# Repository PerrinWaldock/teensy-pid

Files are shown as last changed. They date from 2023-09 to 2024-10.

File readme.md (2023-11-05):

# Teensy-based Intensity Feedback Controller Guide

This repository contains code and PCBs for creating Teensy microcontroller-based feedback controllers. They are used to control the laser intensity on Prometheus because (a) they are relatively inexpensive and (b) they provide faster rise times than similarly-priced analog feedback controllers.

## PCB-free Feedback Controller

The code in the `multistate` branch is currently installed in the Prometheus apparatus. It is running on a Teensy 3.2 because that microcontroller has 5V-tolerant digital inputs, and an inbuilt DAC. It uses two digital signals from the QDGBus digital outputs to select one of four setpoints which are configured over USB. It controls the voltage into a XM-B6H4-0404C-01.

However, this setup has some flaws:
* the inbuilt ADC and DAC are noisy, with only ~8-10 usable bits. This limits the feedback stability shown in the above posts.
* there is no input anti-aliasing filter
* the connections are soldered together on stripboard. The digital input controlling the LSB of the state is currently loose, so the feedback controller occasionally malfunctions when the digital input is not connected to the microcontroller
* the Teensy 3.2 is currently EOL so it is challenging to find a replacement.

A replacement PCB was built that provides the following features:
* input anti-aliasing filtering
* input and output buffering
* input over-voltage protection for both digital and analog inputs
* 16-bit ADCs and DACs
* a faster (600 MHz) microcontroller
* a separate +5V power supply for all analog electronics
* space on the board to mount an XM-B6H4-0404C-01.

The new PCB and its corresponding control code is in the `master` branch of the repository. Below is a guide to the PCB and control code:

## PCB Important Components
The KiCAD design files and schematics are in the schematics folder of this repository. Below is a guide to some components that can be populated or depopulated to change the performance characteristics of the board:
* R1: Populate this to give this board a 50-ohm terminated input. Useful when interfacing with a [PDA100A2](https://www.thorlabs.com/thorproduct.cfm?partnumber=PDA100A2) because they produce a 0-5V output when terminated with a 50 ohm load.
  * One can also modify the values of R1, R2 to remove a DC offset from the input signal, or modify the values of R7 and R9 to amplify the input. Useful if the input is a small signal.
* R3: Populate this to bypass the input op amp. Do not do this without first disconnecting the op amp from by depopulating R2 and R9. Often used when R15 and R17 are populated to use the internal ADC instead of the external ADC (not recommended).
* C1 and R7: Change these values to change the input op amp filter (currently not populated).
* R16 and R18. ONLY POPULATE ONE OF THESE AT A TIME. Used to select 5V or 3.3V reference. If 5V reference is selected (R18), make sure to depopulate R6 so that the input voltage range is the full 0V-5V.
* R34: Populate to use external 5V instead of USB 5V power. DO NOT DO THIS WITHOUT FIRST COVERING THE PIN THAT SUPPLIES POWER ON THE USB CABLE: https://community.octoprint.org/t/put-tape-on-the-5v-pin-why-and-how/13574
* R40: Populate to bypass the output buffer. Do not do this without first disconnecting the op amp by depopulating R41 and FB2.

## Software Important Preprocessor Directives
You can access the following directives in the arduinopid.h file:
* `OUTPUT_SETTLE_DELAY_US` should be set to the response time of the voltage variable attenuator. It is a delay that kicks in immediately after the set point changes from off to on.
  * When the output changes state from off (below the minimum set point) to on (between the minimum and maximum setpoint), the feedback calculation is skipped for the first output, and only the feedforward value is used. This allows the feedback controller to rapidly approach the desired value. However, it takes a finite amount of time for the system to reach the desired value. This delay stops the next feedback measurement from being taken before the system settles to its new state.
* `PIN_REFERENCE0` and `PIN_REFERENCE1` are used to select which preprogrammed set voltage the feedback controller will try to attain.
* `PIN_REFERENCE` can be used as a traditional analog setpoint (NOTE: The PCB is not currently set up to support this)
* `INPUT_MODE` sets the type of input that the feedback controller uses to select its state. `DIGITAL_INPUT` selects preprogrammed set voltage number `PIN_REFERENCE1*2 + PIN_REFERENCE0`, `ANALOG_INPUT` uses the voltage on `PIN_REFERENCE`, and `SOFTWARE_INPUT` only accepts software changes to the set voltage. Note that the `ANALOG_INPUT` mode is not currently well-tested.
  * It may be advantageous to reduce `ANALOGREFERENCERESOLUTION` to 8 or lower to speed up the loop frequency.
* `FEEDFORWARD` enables feedforward control. One can characterize the transfer function of the system via a serial command, then perform corrections to the feedforward function using PID. It generally produces faster rise times than standard PID feedback control.
* `NEGATIVE_OUTPUT` should be set to true if a larger output voltage should produce a smaller input voltage and vice versa.
* `LIMITED_SETPOINT` set to true means that PID control is only active within a certain setpoint range. Set to true to avoid integral wind-up when the output is set to zero or maximum. These
* `SAVE_DATA` will give the option to save PID constants, loop frequency, and feedforward data and load them on startup.

## Serial Commands
Connect the feedback controller using Putty or the Arduino IDE to tune the feedback parameters, adjust the setpoint, loop frequency, and other parameters.

Note that the FeedbackController class in the Prometheus repository uses some of the following serial commands in order to set the laser power to a certain level at specific points in a recipe.

Commands:
* `h` to print the help menu
* `kp=x` to set the proportional constant. `kp?` to print the proportional constant. Similar for `ki` and `kd`.
* `sv0=0.5` to set the 0th preprogammed set voltage to 0.5 volts. similar for `sv1`, `sv2`, and `sv3`. use `sv?` to view all for set voltages. Use `sp` to set the value as an integer instead of as a voltage.
* `ls=0.05` to set the minimum setpoint to 0.05V. Set to some value close to the minimum attainable feedback value. Used to prevent integral wind-up if the system cannot reach the set value.
* `ls=4.5` to set the maximum setpoint to 4.5V. Set to some value close to the maximum attainable feedback value. Used to prevent integral wind-up if the system cannot reach the set value.
* `lf=2000` to set the loop frequency to 2000 Hz. lf? to view the loop frequency. Make sure that the loop period is not less than the time the controller takes to perform a pid calculation.
* `ra=2` to set the number of read averages to four. The formula is <read averages>=2^x where x is an integer -- this ensures that the number of read averages is always a multiple of two, which speeds up the averaging process. Use ra? to view the number of read averages
* `pa=1` to enable feedback control, `pa=0` to disable it
* `po=1` to print sample feedback control values. `po=0` to disable the printed sample feedback control values. A sample string would be `s:6553	 f:6553	 ff:13490	 o:12850	 t:16`, where s refers to the set voltage, f is the feedback voltage, ff is the output voltage the feedforward term recommends, o is the output voltage of the controller, and t is the time the controller took to perform the feedback calculation. All voltages are written as integers, and the time is in microseconds. Write `po=2` to display the values as voltages instead.
* `cf=1` to create the feedforward function. Write `cd?` to print out the calibration data, and `ce?` to print out the calibration extrema (minimum and maximum set voltage).
* `ew=1` to write the feedback constants, loop rate, and calibration data to EEPROM so they are persistent after startup. `ew=0` to read all data from EEPROM. Useful when tuning to restore the feedback controller to a working state.
* `cl=1` to clear the integral term -- helpful if the integral term has spooled up.

Typical usage:
Via the USB serial connection, enter the following comnmands:
* `cf=1` (to calibrate the feedforward function)
* `ce?` (to print the minimum and maximum values that can theoretically be set)
* `sv0=1` (to set the set voltage to 1V. Replace the 1 with a value close to the maximum set voltage found above)
* `po=2` (monitor the output, ensure that it is stable)
* `po=0` (turn off the output)
* set the tuning parameters and loop frequency with `ki=x`,`kp=x`,`kd=0`, `lf=100000`. Ensure that the calculation time does not exceed the loop period. Adjust parameters until performance is satisfactory.

Some of these functions are implemented automatically in FeedbackController class in hardware/FeedbackController in the [Prometheus repository](https://qdg-code.phas.ubc.ca:2633/Perrin/PrometheusPython). This class automatically uses USB commands to assign different set voltages to different set voltage states during the recipe's compile time, then uses digital outputs to select those states while the recipe is executing. It automatically calibrates the feedforward function during compile time.

## Future Work To Do
### Speeding things up
Currently, the microcontroller is set to use a 600 MHz clock. Attaching a heatsink to the processor should allow high clock rates.

Higher clock rates may disrupt communication with the ADC and DAC. To improve the ADC and DAC throughput:
* connect an oscilloscope to the data lines as well as the analog output
* change "#define dacdigwr(p, s) digitalWrite(p, s)" in dac.ino to "#define dacdigwr(p, s) digitalWriteFast(p, s)"
* adjust WRITE_DELAY_NS such that the DAC still consistantly writes the correct value
* similarly, adjust WAIT_TIME_NS and CLOCK_DELAY_NS in adc.ino.
* R21, R22, R23, R24, R25, R26, R30, R31, and R32 may need to be adjusted to a smaller value to accommodate higher clock rates. Choose values that are as large as possible while still allowing the clock to remain high for the specified time in the ADC and DAC datasheets.

### Testing
* The latest version of the PCB (V3.0) has not been tested as a feedback controller for a laser intensity lock.
* Using the analog input as a setpoint also is not well-tested, and may contain bugs.

### New Algorithms
This controller should be usable for a gradient-descent saturated adsorption lock algorithm.

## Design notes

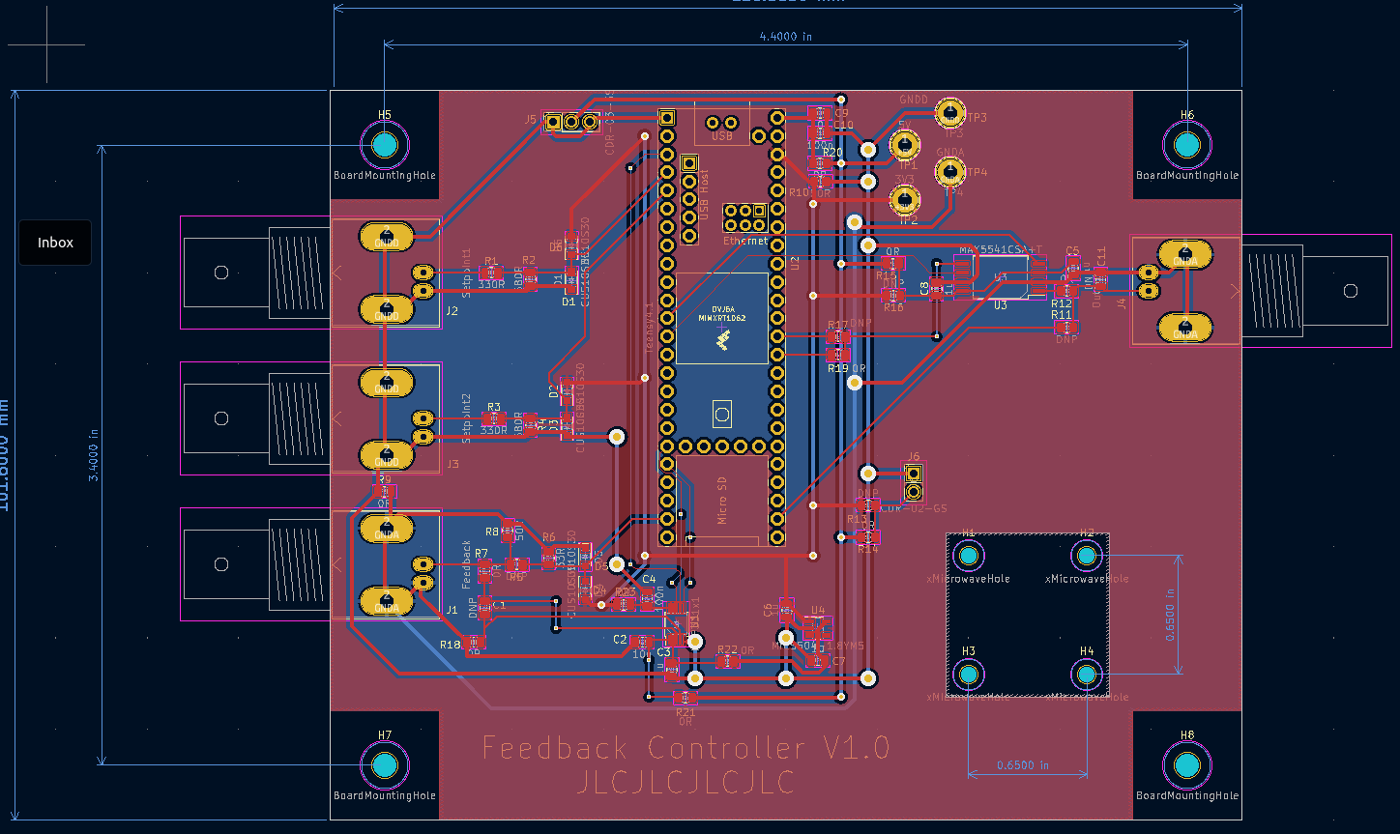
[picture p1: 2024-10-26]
schematics/schematics/feedbackControllerPCB.png

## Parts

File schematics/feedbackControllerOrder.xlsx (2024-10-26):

# | Reference | Qty | Value | Footprint | DNP | Link | Have | Need | Order | ordered
1 | C1, C18 | 2 | 30p | Capacitor_SMD:C_0805_2012Metric | DNP |  |  |  | 0
2 | C2, C6, C12, C15, C26, C28 | 6 | 10u | Capacitor_SMD:C_0805_2012Metric |  | https://www.digikey.ca/en/products/detail/samsung-electro-mechanics/CL21A106KOQNNNG/3894417 |  |  | 12
3 | C3, C5, C8, C9, C10, C13, C16, C25 | 8 | 100n | Capacitor_SMD:C_0805_2012Metric |  | https://www.digikey.ca/en/products/detail/samsung-electro-mechanics/CL21B104KBCNNNC/3886661 |  |  | 16
4 | C4, C20, C21 | 3 | 1n | Capacitor_SMD:C_0805_2012Metric |  | https://www.digikey.ca/en/products/detail/samsung-electro-mechanics/CL21B102KBANFNC/3888082 |  |  | 6
5 | C7, C11, C17, C19, C22, C23, C24, C29 | 8 | 1u | Capacitor_SMD:C_0805_2012Metric |  | https://www.digikey.ca/en/products/detail/samsung-electro-mechanics/CL21B105KAFNNNE/3886724 |  |  | 16
6 | C14 | 1 | 30p | Capacitor_SMD:C_0805_2012Metric |  | https://www.digikey.ca/en/products/detail/kyocera-avx/08055A300JAT2A/1602540 |  |  | 2
7 | C27 | 1 | 10n | Capacitor_SMD:C_0805_2012Metric |  | https://www.digikey.ca/en/products/detail/samsung-electro-mechanics/CL21B103KBANNNC/3886673 |  |  | 2
8 | D1, D2, D3, D4, D5, D6 | 6 | CUS10S30 | Diode_SMD:D_SOD-323_HandSoldering |  | https://www.digikey.ca/en/products/detail/toshiba-semiconductor-and-storage/CUS10S30-H3F/5114299 |  |  | 12
9 | FB1, FB2 | 2 | FerriteBead | Resistor_SMD:R_0805_2012Metric_Pad1.20x1.40mm_HandSolder |  | https://www.digikey.ca/en/products/detail/tai-tech-advanced-electronics-co-ltd/HFZ-2012PF-700T60/17835559 |  |  | 4
10 | H1, H2, H3, H4 | 4 | xMicrowaveHole | MountingHole:MountingHole_2.1mm |  | N/A |  |  | 8
11 | H5, H6, H7, H8 | 4 | BoardMountingHole | MountingHole:MountingHole_3.2mm_M3 |  | N/A |  |  | 8
12 | J1 | 1 | Feedback | Connector_Coaxial:BNC_Amphenol_B6252HB-NPP3G-50_Horizontal |  | Don’t Need |  |  | 2
13 | J2 | 1 | Setpoint1 | Connector_Coaxial:BNC_Amphenol_B6252HB-NPP3G-50_Horizontal |  | Don’t Need |  |  | 2
14 | J3 | 1 | Setpoint2 | Connector_Coaxial:BNC_Amphenol_B6252HB-NPP3G-50_Horizontal |  | Don’t Need |  |  | 2
15 | J4 | 1 | Output | Connector_Coaxial:BNC_Amphenol_B6252HB-NPP3G-50_Horizontal |  | Don’t Need |  |  | 2
16 | J5 | 1 | CDR-03-GS | Connector_PinSocket_2.54mm:PinSocket_1x03_P2.54mm_Vertical |  | Don’t Need |  |  | 2
17 | J6 | 1 | CDR-02-GS | Connector_PinHeader_2.54mm:PinHeader_1x02_P2.54mm_Vertical |  | Don’t Need |  |  | 2
18 | JP1, JP2, JP3 | 3 | SolderJumper_2_Open | Jumper:SolderJumper-2_P1.3mm_Open_Pad1.0x1.5mm |  | N/A |  |  | 6
19 | R1 | 1 | 50R | Resistor_SMD:R_0805_2012Metric | DNP |  |  |  | 0
20 | R2, R6, R7, R9, R13, R16, R19, R20, R28, R33, R34, R37, R41, R42, R43, R46 | 16 | 0R | Resistor_SMD:R_0805_2012Metric |  | https://www.digikey.ca/en/products/detail/stackpole-electronics-inc/RMCF0805ZT0R00/1756901 |  |  | 32
21 | R3, R18, R40, R44, R45 | 5 | 0R | Resistor_SMD:R_0805_2012Metric | DNP |  |  |  | 0
22 | R4, R15 | 2 | 1k | Resistor_SMD:R_0805_2012Metric | DNP |  |  |  | 0
23 | R5 | 1 | 350R | Resistor_SMD:R_0805_2012Metric |  | https://www.digikey.ca/en/products/detail/yageo/RC0805FR-07316RL/727856 |  |  | 2
24 | R8, R10, R27, R29 | 4 | 1k | Resistor_SMD:R_0805_2012Metric |  | https://www.digikey.ca/en/products/detail/stackpole-electronics-inc/RNCP0805FTD1K00/2240229 |  |  | 8
25 | R11 | 1 | 160R | Resistor_SMD:R_0805_2012Metric |  | https://www.digikey.ca/en/products/detail/koa-speer-electronics-inc/RK73H2ATTD1600F/10234348 |  |  | 2
26 | R12, R14 | 2 | 2k | Resistor_SMD:R_0805_2012Metric |  | https://www.digikey.ca/en/products/detail/stackpole-electronics-inc/RMCF0805FT2K00/1760249 |  |  | 4
27 | R17 | 1 | 2k | Resistor_SMD:R_0805_2012Metric | DNP |  |  |  | 0
28 | R21, R22, R23, R24, R25, R26, R30, R31, R32 | 9 | 10R | Resistor_SMD:R_0805_2012Metric |  | https://www.digikey.ca/en/products/detail/stackpole-electronics-inc/RMCF0805FT10R0/1760155 |  |  | 18
29 | R35 | 1 | 150R | Resistor_SMD:R_0805_2012Metric |  | https://www.digikey.ca/en/products/detail/koa-speer-electronics-inc/RK73H2ATTD1500F/10234167 |  |  | 2
30 | R36 | 1 | 100k | Resistor_SMD:R_0805_2012Metric | DNP |  |  |  | 0
31 | R38, R39 | 2 | 10k | Resistor_SMD:R_0805_2012Metric |  | https://www.digikey.ca/en/products/detail/vishay-dale/CRCW080510K0FKEAC/7928398 |  |  | 4
32 | TP1 | 1 | ADC_CONV | TestPoint:TestPoint_Loop_D2.50mm_Drill1.0mm |  | N/A |  |  | 2
33 | TP2 | 1 | ADC_DAT | TestPoint:TestPoint_Loop_D2.50mm_Drill1.0mm |  | N/A |  |  | 2
34 | TP3 | 1 | ADC_CLK | TestPoint:TestPoint_Loop_D2.50mm_Drill1.0mm |  | N/A |  |  | 2
35 | TP4 | 1 | DAC_CS | TestPoint:TestPoint_Loop_D2.50mm_Drill1.0mm |  | N/A |  |  | 2
36 | TP5 | 1 | DAC_DIN | TestPoint:TestPoint_Loop_D2.50mm_Drill1.0mm |  | N/A |  |  | 2
37 | TP6 | 1 | DAC_CLK | TestPoint:TestPoint_Loop_D2.50mm_Drill1.0mm |  | N/A |  |  | 2
38 | TP7 | 1 | +5V | TestPoint:TestPoint_Loop_D2.50mm_Drill1.0mm |  | N/A |  |  | 2
39 | TP8 | 1 | +3.3V | TestPoint:TestPoint_Loop_D2.50mm_Drill1.0mm |  | N/A |  |  | 2
40 | TP9 | 1 | GNDD | TestPoint:TestPoint_Loop_D2.50mm_Drill1.0mm |  | N/A |  |  | 2
41 | TP10 | 1 | GNDA | TestPoint:TestPoint_Loop_D2.50mm_Drill1.0mm |  | N/A |  |  | 2
42 | TP11 | 1 | +5VA | TestPoint:TestPoint_Loop_D2.50mm_Drill1.0mm |  | N/A |  |  | 2
43 | TP12 | 1 | +9V | TestPoint:TestPoint_Loop_D2.50mm_Drill1.0mm |  | N/A |  |  | 2
44 | U1, U6 | 2 | RS621 | Package_TO_SOT_SMD:SOT-23-5_HandSoldering |  | https://www.digikey.ca/en/products/detail/runic-technology/RS621KXF/14544643 |  |  | 4
45 | U2 | 1 | MCP331x1 | Package_SO:MSOP-10_3x3mm_P0.5mm |  | https://www.digikey.ca/en/products/detail/microchip-technology/MCP33131-10-E-MS/9757740 |  |  | 2
46 | U3 | 1 | TXU0104D | Package_SO:SOIC-14_3.9x8.7mm_P1.27mm |  | https://www.digikey.ca/en/products/detail/texas-instruments/TXB0104DR/1629101 |  |  | 2
47 | U4 | 1 | Teensy4.0 | Teensy:Teensy40 |  | https://www.digikey.ca/en/products/detail/sparkfun-electronics/DEV-15583/10384551 |  |  | 2
48 | U5 | 1 | MAX5541CSA+T | Package_SO:SOIC-8_3.9x4.9mm_P1.27mm |  | https://www.digikey.ca/en/products/detail/analog-devices-inc-maxim-integrated/MAX5541CSA-T/1780972 |  |  | 2
49 | U7 | 1 | MIC5504-3.3YM5 | Package_TO_SOT_SMD:SOT-23-5 |  | https://www.digikey.ca/en/products/detail/microchip-technology/MIC5504-1-8YM5-TR/5209404 |  |  | 2
50 | U8 | 1 | TC1014-2.5VCT713 | Package_TO_SOT_SMD:SOT-23-5 |  | https://www.digikey.ca/en/products/detail/microchip-technology/TC1014-2-5VCT713/443102 |  |  | 2
51 | U9 | 1 | TC1014-1.8VCT713 | Package_TO_SOT_SMD:SOT-23-5 |  | https://www.digikey.ca/en/products/detail/microchip-technology/TC1014-1-8VCT713/443100 |  |  | 2
52 | U10 | 1 | NJM2882F05-TE1 | Package_TO_SOT_SMD:SOT-23-5_HandSoldering |  | https://www.digikey.ca/en/products/detail/nisshinbo-micro-devices-inc/NJM2882F05-TE1/10671911 |  |  | 2
53 | U11 | 1 | IB0509LS-1WR3 | Misc:IB05_LS-1WR3 |  | https://www.digikey.ca/en/products/detail/mornsun-america-llc/IB0509LS-1WR3/16571428?s=N4IgTCBcDaIJICEAMBWJBOAMgZQLQEYB1AJQGYQBdAXyA |  |  | 2

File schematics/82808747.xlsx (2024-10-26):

# | QUANTITY | PART NUMBER | MANUFACTURER PART NUMBER | DESCRIPTION | CUSTOMER REFERENCE | BACKORDER | UNIT PRICE | EXTENDED PRICE
1 | 2 | 1568-DEV-20359-ND | DEV-20359 | TEENSY 4.1 WITHOUT ETHERNET |  | 0 | 43.56 | 87.12
2 | 3 | MCP33131-10-E/MS-ND | MCP33131-10-E/MS | IC ADC 16BIT SAR 10MSOP |  | 0 | 7.5 | 22.50
3 | 3 | MAX5541CSA+TCT-ND | MAX5541CSA+T | IC DAC 16BIT V-OUT 8SOIC |  | 0 | 21.26 | 63.78
4 | 5 | 576-4879-1-ND | MIC5504-1.8YM5-TR | IC REG LINEAR 1.8V 300MA SOT23-5 |  | 0 | 0.24 | 1.20
5 | 10 | 3565-RS621KXFCT-ND | RS621KXF | IC CMOS 1 CIRCUIT SOT23-5 |  | 0 | 0.678 | 6.78
6 | 20 | CUS10S30H3FCT-ND | CUS10S30,H3F | DIODE SCHOTTKY 30V 1A USC |  | 0 | 0.363 | 7.26
7 | 12 | WM5514-ND | 0731375003 | CONN BNC RCPT R/A 50 OHM PCB |  | 0 | 3.45 | 41.40
8 | 10 | 2057-CDR-03-TS-ND | CDR-03-TS | HEADER VERT TH TIN 3POS .1" SING |  | 0 | 0.258 | 2.58
9 | 3 | 2057-CDR-02-GS-ND | CDR-02-GS | HEADER VERT TH GOLD 2POS .1" SIN |  | 0 | 0.25 | 0.75
10 | 5 | 2057-CDH-02-ND | CDH-02 | CONN PLUG HSG 2POS 2.54MM |  | 0 | 0.25 | 1.25
11 | 10 | 2057-CDH-C-G-RCT-ND | CDH-C-G-R | CONTACT CRIMP FOR CDH-XX GOLD |  | 0 | 0.241 | 2.41
12 | 10 | 1276-2424-1-ND | CL21B102KBANFNC | CAP CER 1000PF 50V X7R 0805 |  | 0 | 0.056 | 0.56
13 | 20 | 1276-6455-1-ND | CL21A106KOQNNNG | CAP CER 10UF 16V X5R 0805 |  | 0 | 0.104 | 2.08
14 | 20 | 1276-1066-1-ND | CL21B105KAFNNNE | CAP CER 1UF 25V X7R 0805 |  | 0 | 0.091 | 1.82
15 | 10 | 13-RC0805FR-10330RLCT-ND | RC0805FR-10330RL | RES 330 OHM 1% 1/8W 0805 |  | 0 | 0.036 | 0.36
16 | 10 | 311-680CRCT-ND | RC0805FR-07680RL | RES 680 OHM 1% 1/8W 0805 |  | 0 | 0.036 | 0.36
17 | 20 | 1276-1003-1-ND | CL21B104KBCNNNC | CAP CER 0.1UF 50V X7R 0805 |  | 0 | 0.062 | 1.24
18 | 10 | 2019-RK73H2ATTD18R0FCT-ND | RK73H2ATTD18R0F | RES 18 OHM 1% 1/4W 0805 |  | 0 | 0.055 | 0.55
19 | 10 | 2019-RK73H2ATTD30R9FCT-ND | RK73H2ATTD30R9F | RES 30.9 OHM 1% 1/4W 0805 |  | 0 | 0.055 | 0.55
20 | 10 | RNCP0805FTD49R9CT-ND | RNCP0805FTD49R9 | RES 49.9 OHM 1% 1/4W 0805 |  | 0 | 0.105 | 1.05
21 | 10 | 2019-RK73H2ATTD1600FCT-ND | RK73H2ATTD1600F | RES 160 OHM 1% 1/4W 0805 |  | 0 | 0.055 | 0.55
22 | 50 | RMCF0805ZT0R00CT-ND | RMCF0805ZT0R00 | RES 0 OHM JUMPER 1/8W 0805 |  | 0 | 0.0144 | 0.72
23 | 10 | RNCP0805FTD1R00CT-ND | RNCP0805FTD1R00 | RES 1 OHM 1% 1/4W 0805 |  | 0 | 0.105 | 1.05

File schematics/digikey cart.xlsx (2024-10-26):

Index | Quantity | Part Number | Manufacturer Part Number | Description | Customer Reference | Available | Backorder | Unit Price | Extended Price CAD
1 | 4 | 2057-RF1-01K-D-00-50-BK-HDW-ND | RF1-01K-D-00-50-BK-HDW | BNC RA PCB 50 4GHZ ZINC BODY NI |  | 4 | 0 | 3.48 | 13.92
2 | 2 | MAX5541CSA+-ND | MAX5541CSA+ | IC DAC 16BIT V-OUT 8SOIC |  | 2 | 0 | 20.7 | 41.40
3 | 2 | MCP33131D-10T-I/MSCT-ND | MCP33131D-10T-I/MS | IC ADC 16BIT SAR 10MSOP |  | 2 | 0 | 15.13 | 30.26
4 | 10 | 1276-1003-1-ND | CL21B104KBCNNNC | CAP CER 0.1UF 50V X7R 0805 |  | 10 | 0 | 0.065 | 0.65
5 | 20 | 1276-1066-1-ND | CL21B105KAFNNNE | CAP CER 1UF 25V X7R 0805 |  | 20 | 0 | 0.096 | 1.92
6 | 10 | 1276-6454-1-ND | CL21A106KAYNNNG | CAP CER 10UF 25V X5R 0805 |  | 10 | 0 | 0.188 | 1.88
7 | 10 | CUS10S30H3FCT-ND | CUS10S30,H3F | DIODE SCHOTTKY 30V 1A USC |  | 10 | 0 | 0.388 | 3.88
8 | 25 | RMCF0805ZT0R00CT-ND | RMCF0805ZT0R00 | RES 0 OHM JUMPER 1/8W 0805 |  | 25 | 0 | 0.02 | 0.50
9 | 5 | 2057-CDR-03-GS-ND | CDR-03-GS | HEADER VERT TH GOLD 3POS .1" SIN |  | 5 | 0 | 0.32 | 1.60
10 | 5 | 2057-CDR-02-GS-ND | CDR-02-GS | HEADER VERT TH GOLD 2POS .1" SIN |  | 5 | 0 | 0.26 | 1.30
11 | 10 | 13-RC0805FR-13330RLCT-ND | RC0805FR-13330RL | RES 330 OHM 1% 1/8W 0805 |  | 10 | 0 | 0.052 | 0.52
12 | 10 | 511-SDR10EZPF49R9CT-ND | SDR10EZPF49R9 | HIGH ANTI-SURGE THICK FILM CHIP |  | 10 | 0 | 0.408 | 4.08
13 | 10 | 311-680CRCT-ND | RC0805FR-07680RL | RES 680 OHM 1% 1/8W 0805 |  | 10 | 0 | 0.052 | 0.52
14 | 3 | 576-4879-1-ND | MIC5504-1.8YM5-TR | IC REG LINEAR 1.8V 300MA SOT23-5 |  | 3 | 0 | 0.27 | 0.81
15 | 3 | 2057-CDH-02-ND | CDH-02 | CONN PLUG HSG 2POS 2.54MM |  | 0 | 3 | 0.27 | 0.81
16 | 10 | 2057-CDH-C-G-RCT-ND | CDH-C-G-R | CONTACT CRIMP FOR CDH-XX GOLD |  | 10 | 0 | 0.253 | 2.53
17 | 10 | P19220CT-ND | ERJ-6DQJ1R0V | RES SMD 1 OHM 5% 1/2W 0805 |  | 10 | 0 | 0.322 | 3.22
18 | 10 | P19220CT-ND | ERJ-6DQJ1R0V | RES SMD 1 OHM 5% 1/2W 0805 |  | 10 | 0 | 0.322 | 3.22

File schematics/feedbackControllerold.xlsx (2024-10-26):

Source: | /home/perrin/pcsync/BCITUBC/electronics/SimpleFeedbackController/feedbackController/feedbackController.kicad_sch
Date: | Sat 19 Aug 2023 12:48:53 PM
Tool: | Eeschema 7.0.6-7.0.6~ubuntu22.04.1
Generator: | /usr/share/kicad/plugins/bom_csv_grouped_by_value.py
Component Count: | 73
Collated Components:
Item | Qty | Reference(s) | Value | LibPart | Footprint | Datasheet | DNP | soldered
1 | 1 | C1 | 1n | Device:C | Capacitor_SMD:C_0805_2012Metric | ~
2 | 4 | C2, C9, C12, C14 | 10u | Device:C | Capacitor_SMD:C_0805_2012Metric | ~
3 | 5 | C3, C5, C6, C7, C8 | 1u | Device:C | Capacitor_SMD:C_0805_2012Metric | ~
4 | 4 | C4, C10, C13, C15 | 100n | Device:C | Capacitor_SMD:C_0805_2012Metric | ~
5 | 1 | C11 | 1n | Device:C | Capacitor_SMD:C_0805_2012Metric | ~ | DNP
6 | 6 | D1, D2, D3, D4, D5, D6 | CUS10S30 | pspice:DIODE | Diode_SMD:D_SOD-323_HandSoldering | ~
7 | 4 | H1, H2, H3, H4 | xMicrowaveHole | Mechanical:MountingHole | MountingHole:MountingHole_2.1mm | ~
8 | 4 | H5, H6, H7, H8 | BoardMountingHole | Mechanical:MountingHole | MountingHole:MountingHole_3.2mm_M3 | ~
9 | 1 | J1 | Feedback | Connector:Conn_Coaxial | Connector_Coaxial:BNC_Amphenol_B6252HB-NPP3G-50_Horizontal | ~
10 | 1 | J2 | Setpoint1 | Connector:Conn_Coaxial | Connector_Coaxial:BNC_Amphenol_B6252HB-NPP3G-50_Horizontal | ~
11 | 1 | J3 | Setpoint2 | Connector:Conn_Coaxial | Connector_Coaxial:BNC_Amphenol_B6252HB-NPP3G-50_Horizontal | ~
12 | 1 | J4 | Output | Connector:Conn_Coaxial | Connector_Coaxial:BNC_Amphenol_B6252HB-NPP3G-50_Horizontal | ~
13 | 1 | J5 | CDR-03-GS | Connector:Conn_01x03_Pin | Connector_PinSocket_2.54mm:PinSocket_1x03_P2.54mm_Vertical | ~
14 | 1 | J6 | CDR-02-GS | Connector:Conn_01x02_Pin | Connector_PinHeader_2.54mm:PinHeader_1x02_P2.54mm_Vertical | ~
15 | 2 | R1, R3 | 330R | Device:R_US | Resistor_SMD:R_0805_2012Metric | ~
16 | 2 | R2, R4 | 680R | Device:R_US | Resistor_SMD:R_0805_2012Metric | ~
17 | 1 | R5 | 18R | Device:R_US | Resistor_SMD:R_0805_2012Metric | ~ | DNP
18 | 1 | R6 | 33R | Device:R_US | Resistor_SMD:R_0805_2012Metric | ~
19 | 1 | R7 | 160R | Device:R_US | Resistor_SMD:R_0805_2012Metric | ~
20 | 2 | R8, R10 | 50R | Device:R_US | Resistor_SMD:R_0805_2012Metric | ~
21 | 11 | R9, R14, R15, R18, R19, R20, R21, R22, R23, R24, R29 | 0R | Device:R_US | Resistor_SMD:R_0805_2012Metric | ~
22 | 1 | R11 | 1k | Device:R_US | Resistor_SMD:R_0805_2012Metric | ~ | DNP
23 | 4 | R12, R16, R17, R25 | 0R | Device:R_US | Resistor_SMD:R_0805_2012Metric | ~ | DNP
24 | 1 | R13 | DNP | Device:R_US | Resistor_SMD:R_0805_2012Metric | ~
25 | 2 | R26, R27 | 1R | Device:R_US | Resistor_SMD:R_0805_2012Metric | ~
26 | 1 | TP1 | 5V | Connector:TestPoint | TestPoint:TestPoint_Loop_D3.80mm_Drill2.0mm | ~
27 | 1 | TP2 | 3V3 | Connector:TestPoint | TestPoint:TestPoint_Loop_D3.80mm_Drill2.0mm | ~
28 | 1 | TP3 | GNDD | Connector:TestPoint | TestPoint:TestPoint_Loop_D3.80mm_Drill2.0mm | ~
29 | 1 | TP4 | GNDA | Connector:TestPoint | TestPoint:TestPoint_Loop_D3.80mm_Drill2.0mm | ~
30 | 1 | U1 | MCP331x1 | Jakub:MCP331x1 | Package_SO:MSOP-10_3x3mm_P0.5mm | https://ww1.microchip.com/downloads/en/DeviceDoc/MCP33131D-Data-Sheet-DS20005947B.pdf |  | x
31 | 1 | U2 | Teensy4.1 | Teensy:Teensy4.1 | Teensy:Teensy41
32 | 1 | U3 | MAX5541CSA+T | MAX5541:MAX5541CSA+T | SOIC127P600X175-8N | https://www.analog.com/media/en/technical-documentation/data-sheets/MAX5541.pdf |  | x
33 | 1 | U4 | MIC5504-1.8YM5 | Regulator_Linear:MIC5504-1.8YM5 | Package_TO_SOT_SMD:SOT-23-5 | http://ww1.microchip.com/downloads/en/DeviceDoc/MIC550X.pdf
34 | 2 | U5, U6 | ~ | Misc:RS621KXF | Package_TO_SOT_SMD:SOT-23-5_HandSoldering

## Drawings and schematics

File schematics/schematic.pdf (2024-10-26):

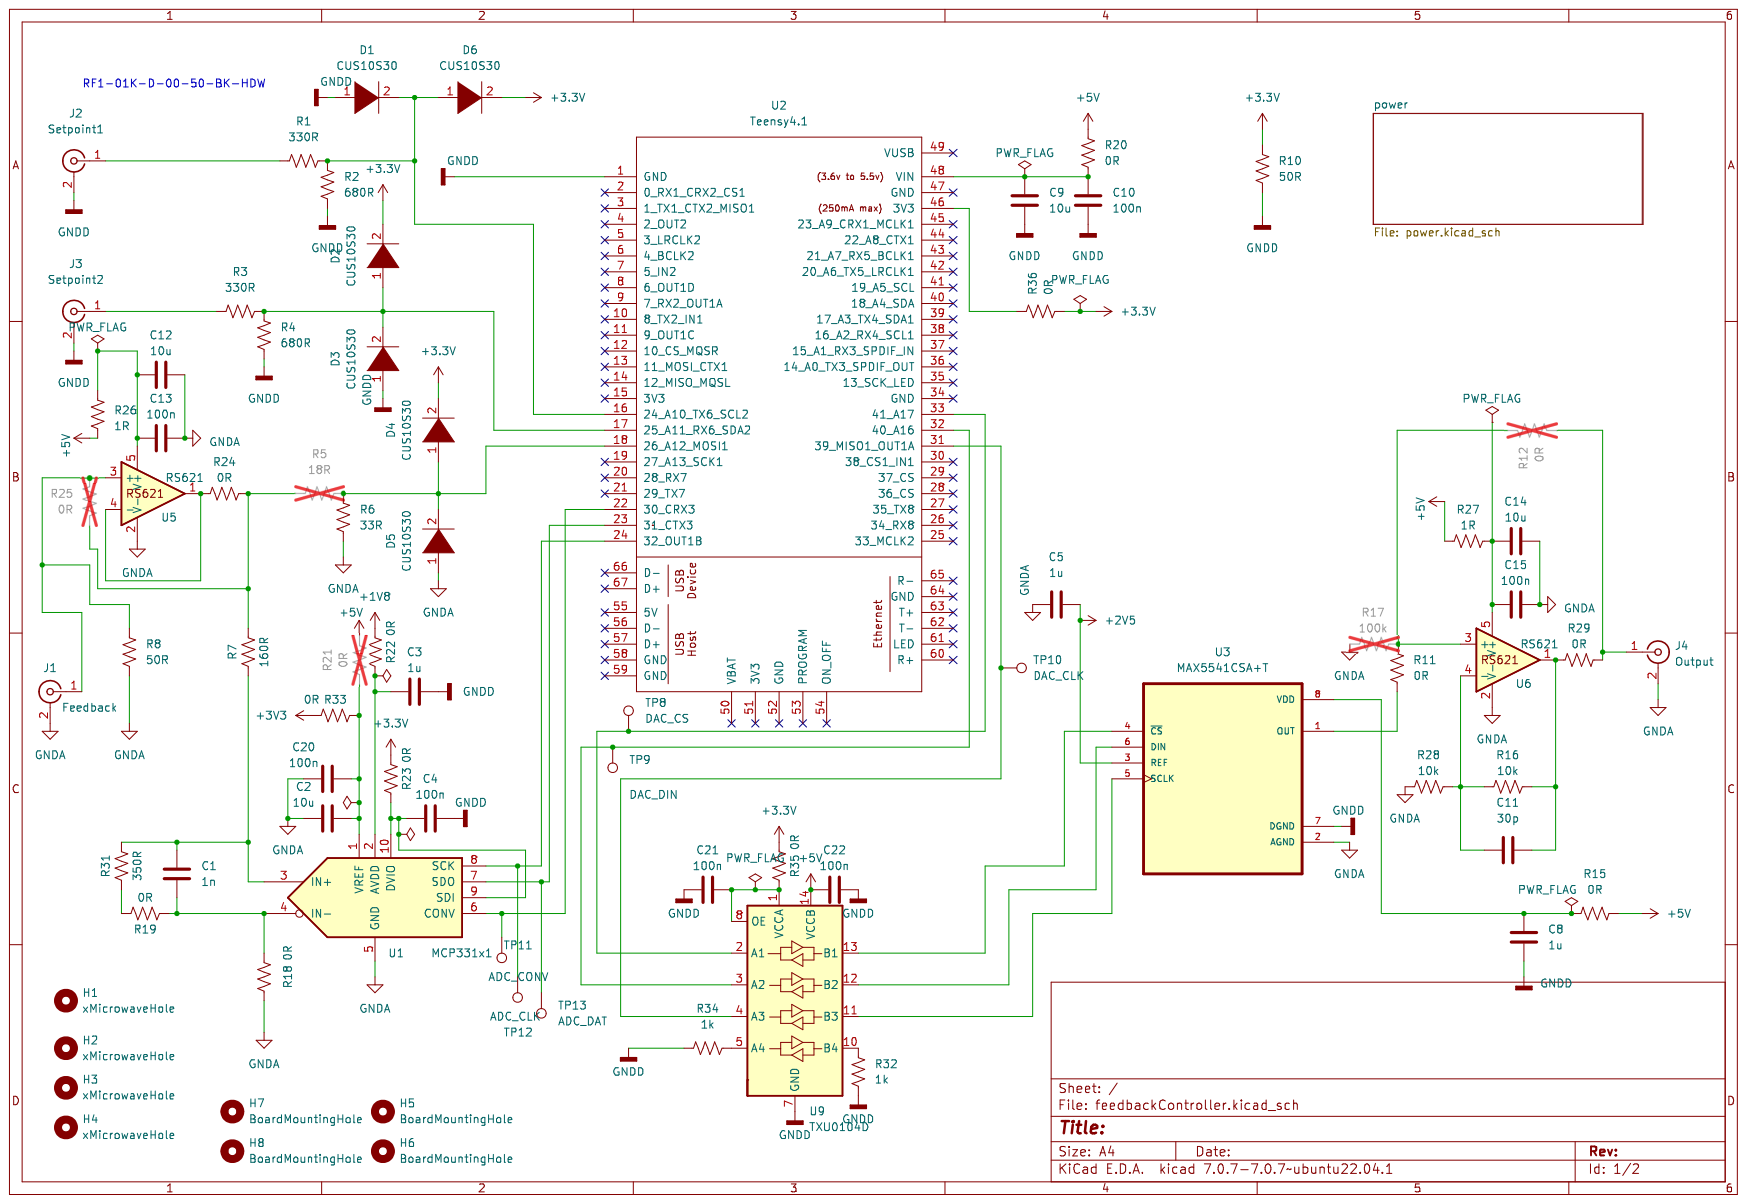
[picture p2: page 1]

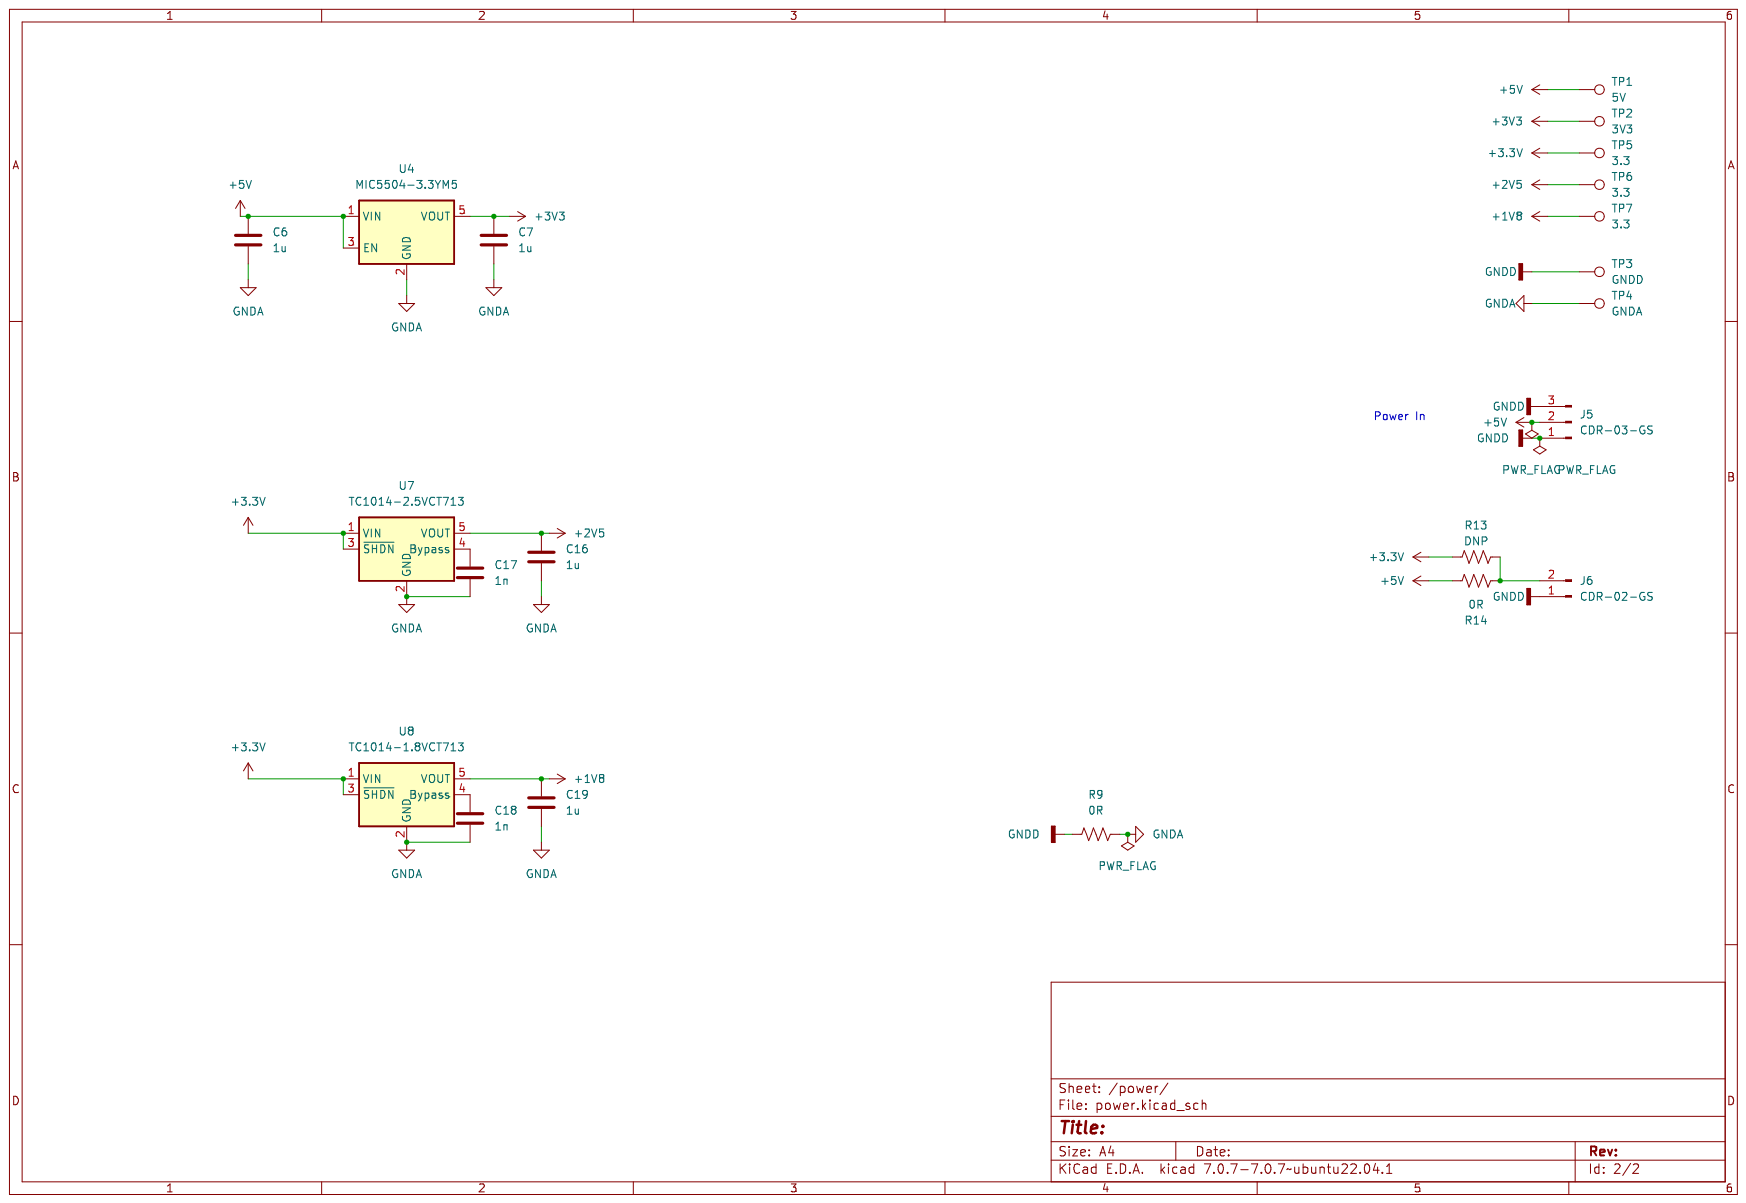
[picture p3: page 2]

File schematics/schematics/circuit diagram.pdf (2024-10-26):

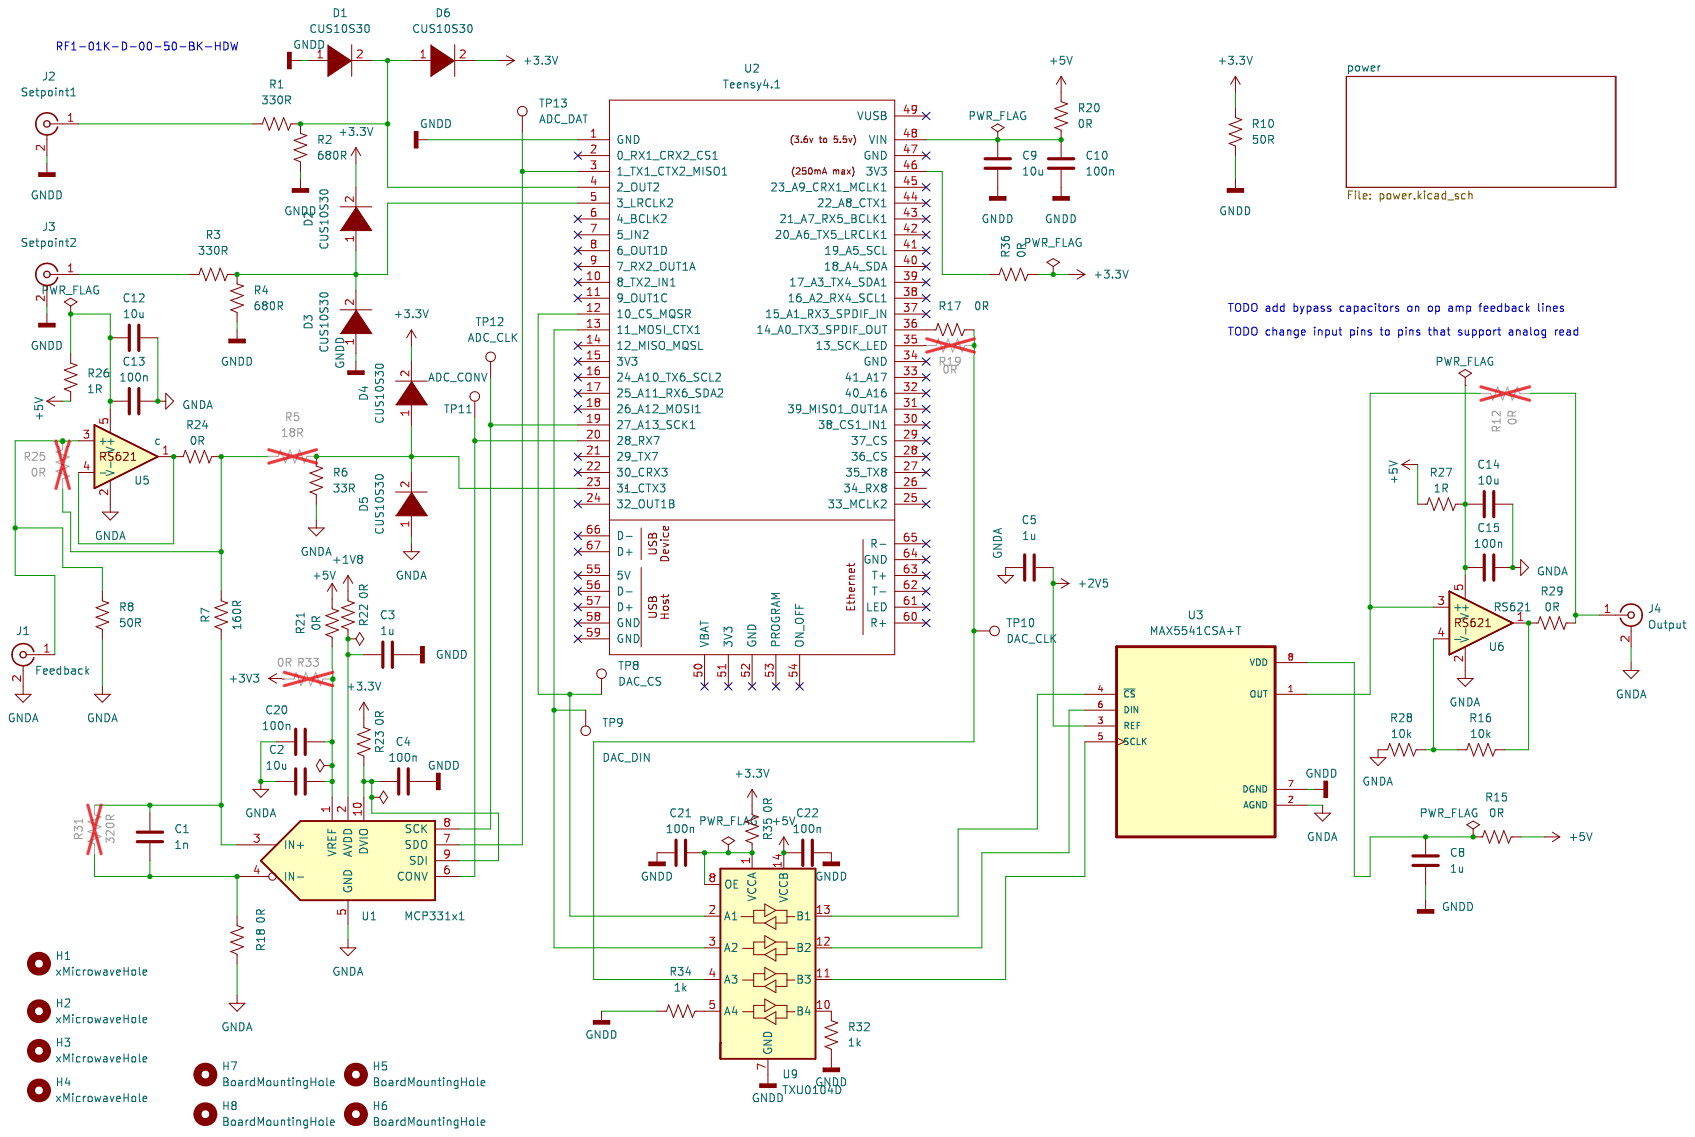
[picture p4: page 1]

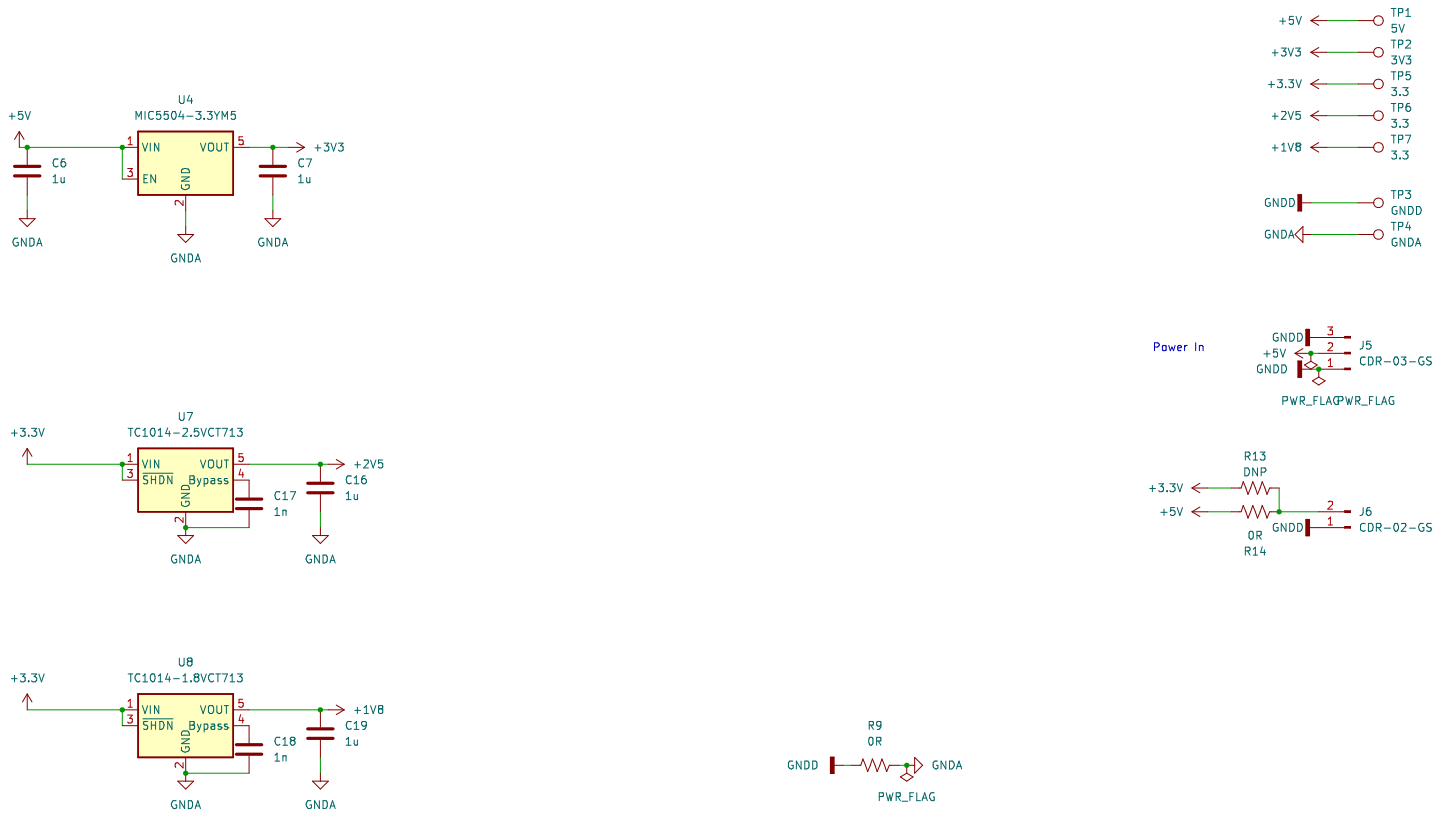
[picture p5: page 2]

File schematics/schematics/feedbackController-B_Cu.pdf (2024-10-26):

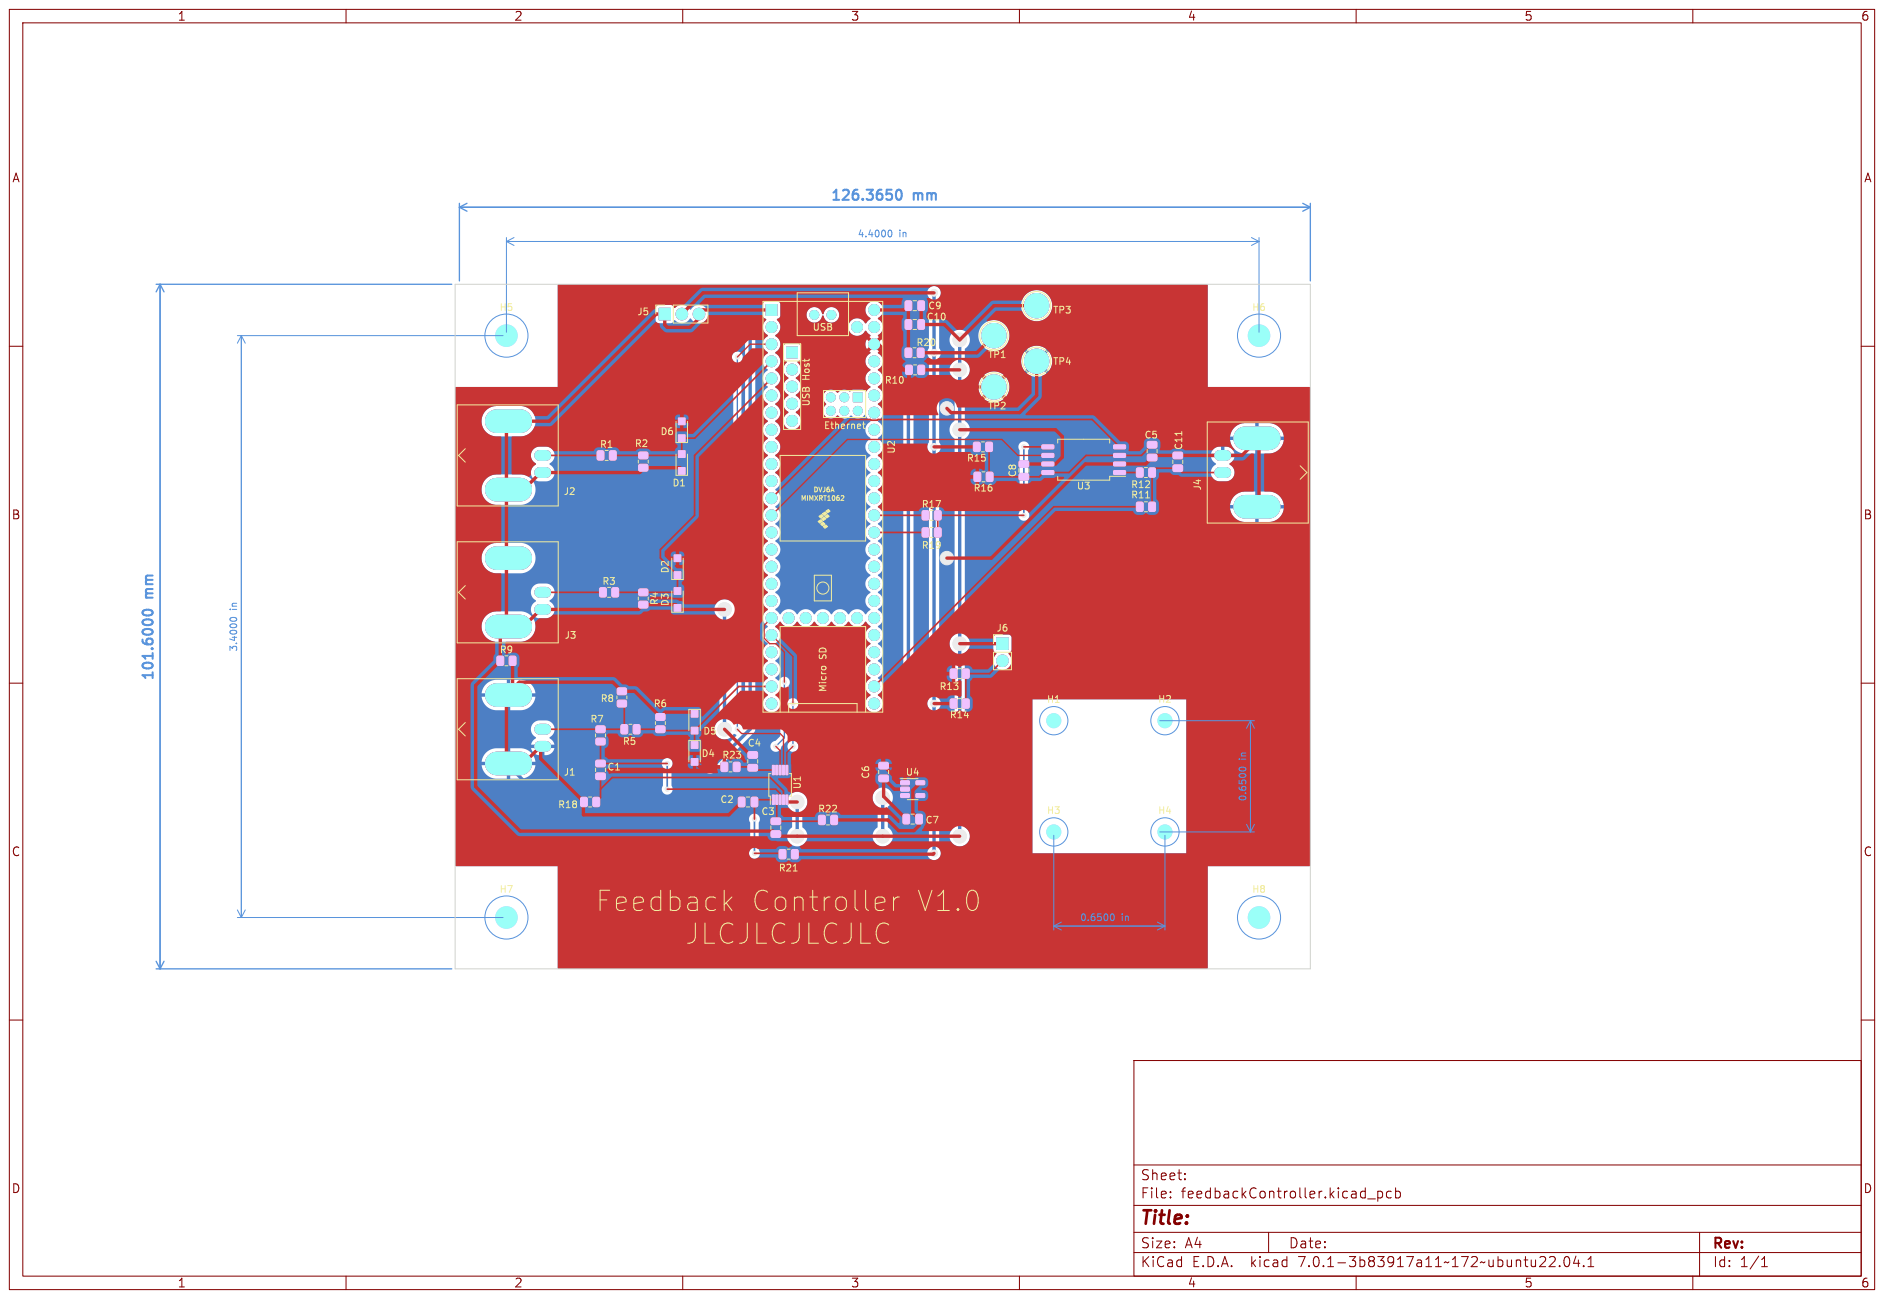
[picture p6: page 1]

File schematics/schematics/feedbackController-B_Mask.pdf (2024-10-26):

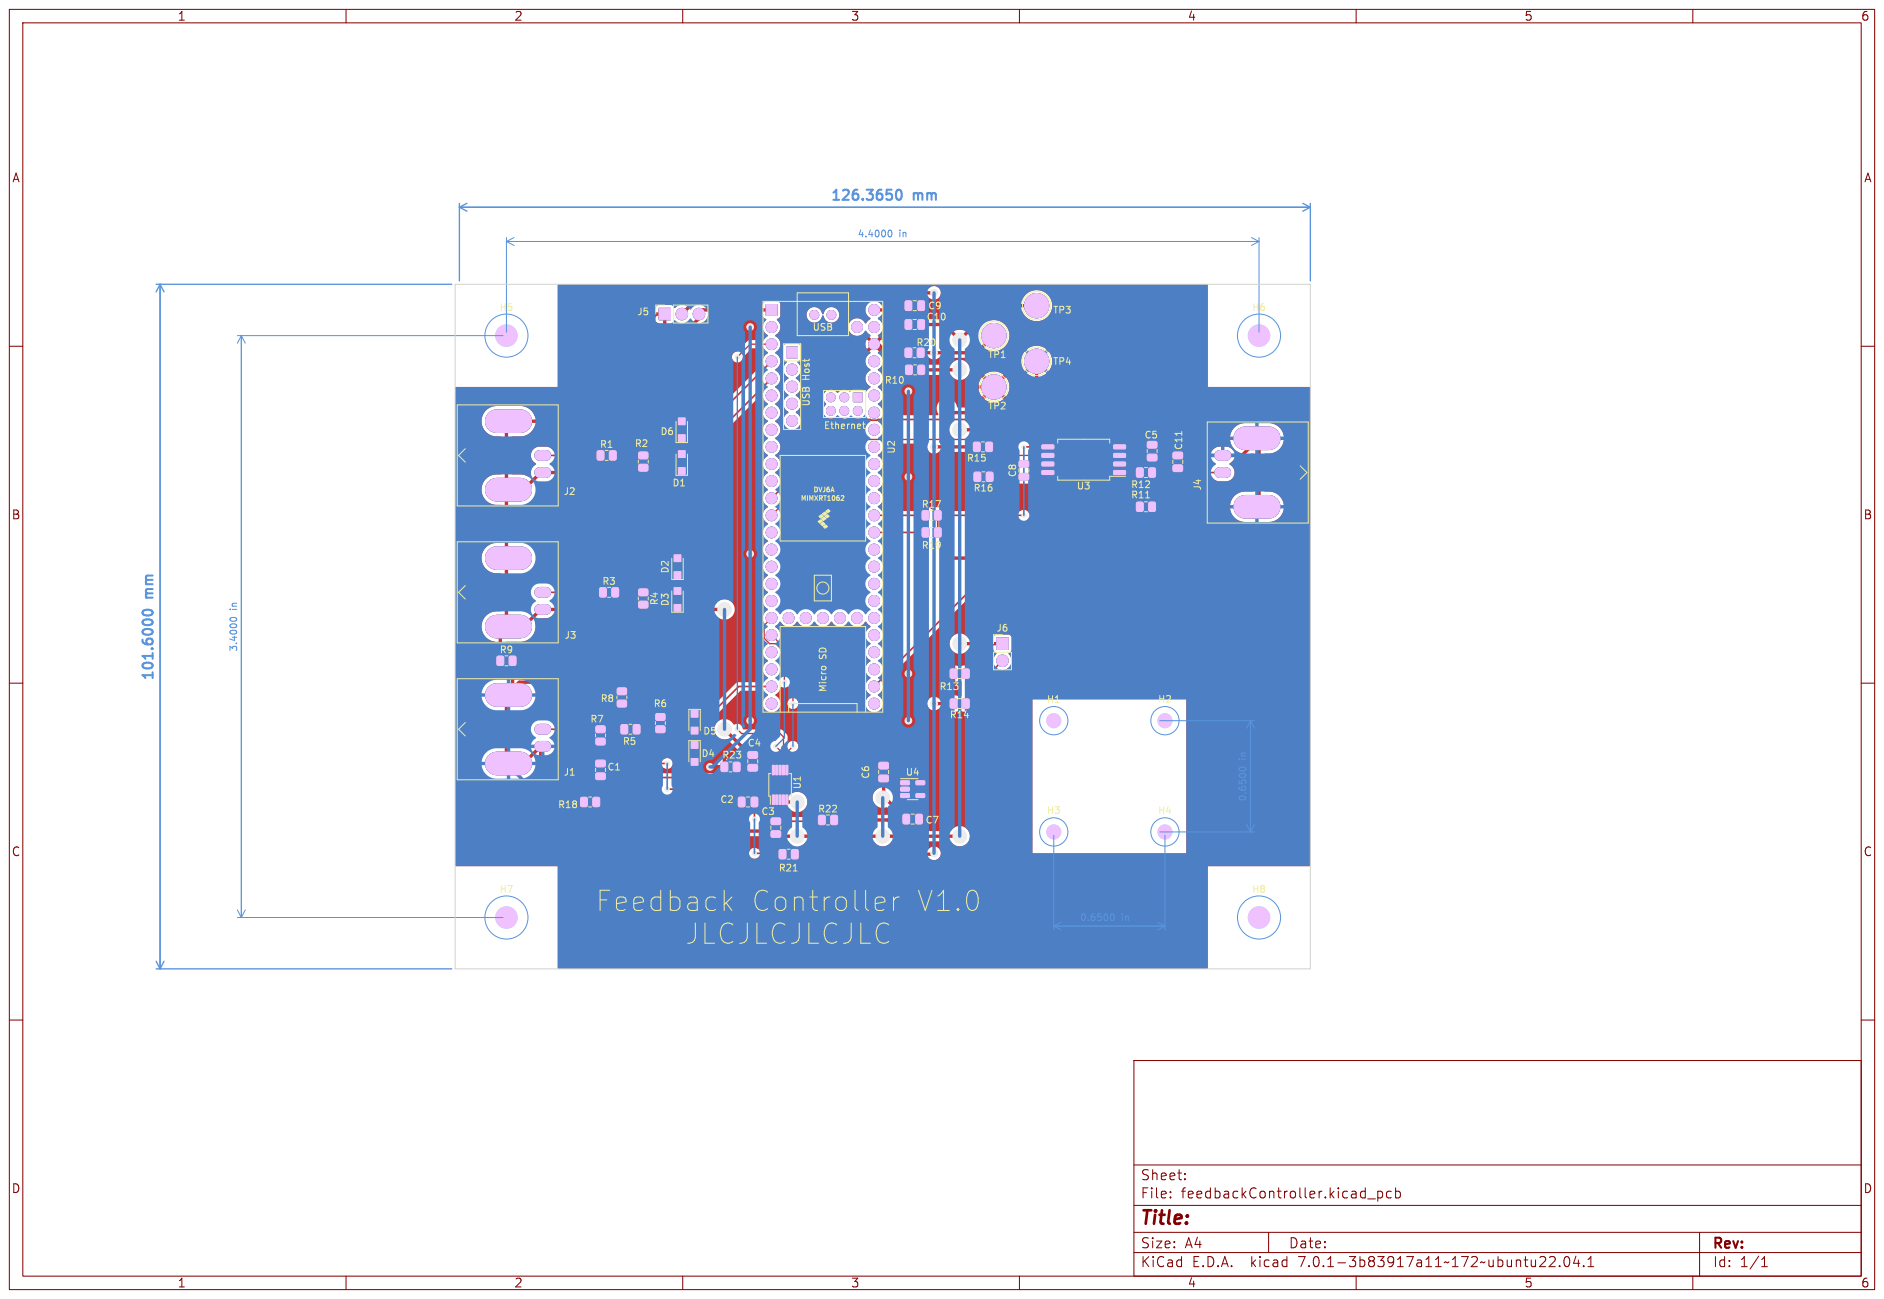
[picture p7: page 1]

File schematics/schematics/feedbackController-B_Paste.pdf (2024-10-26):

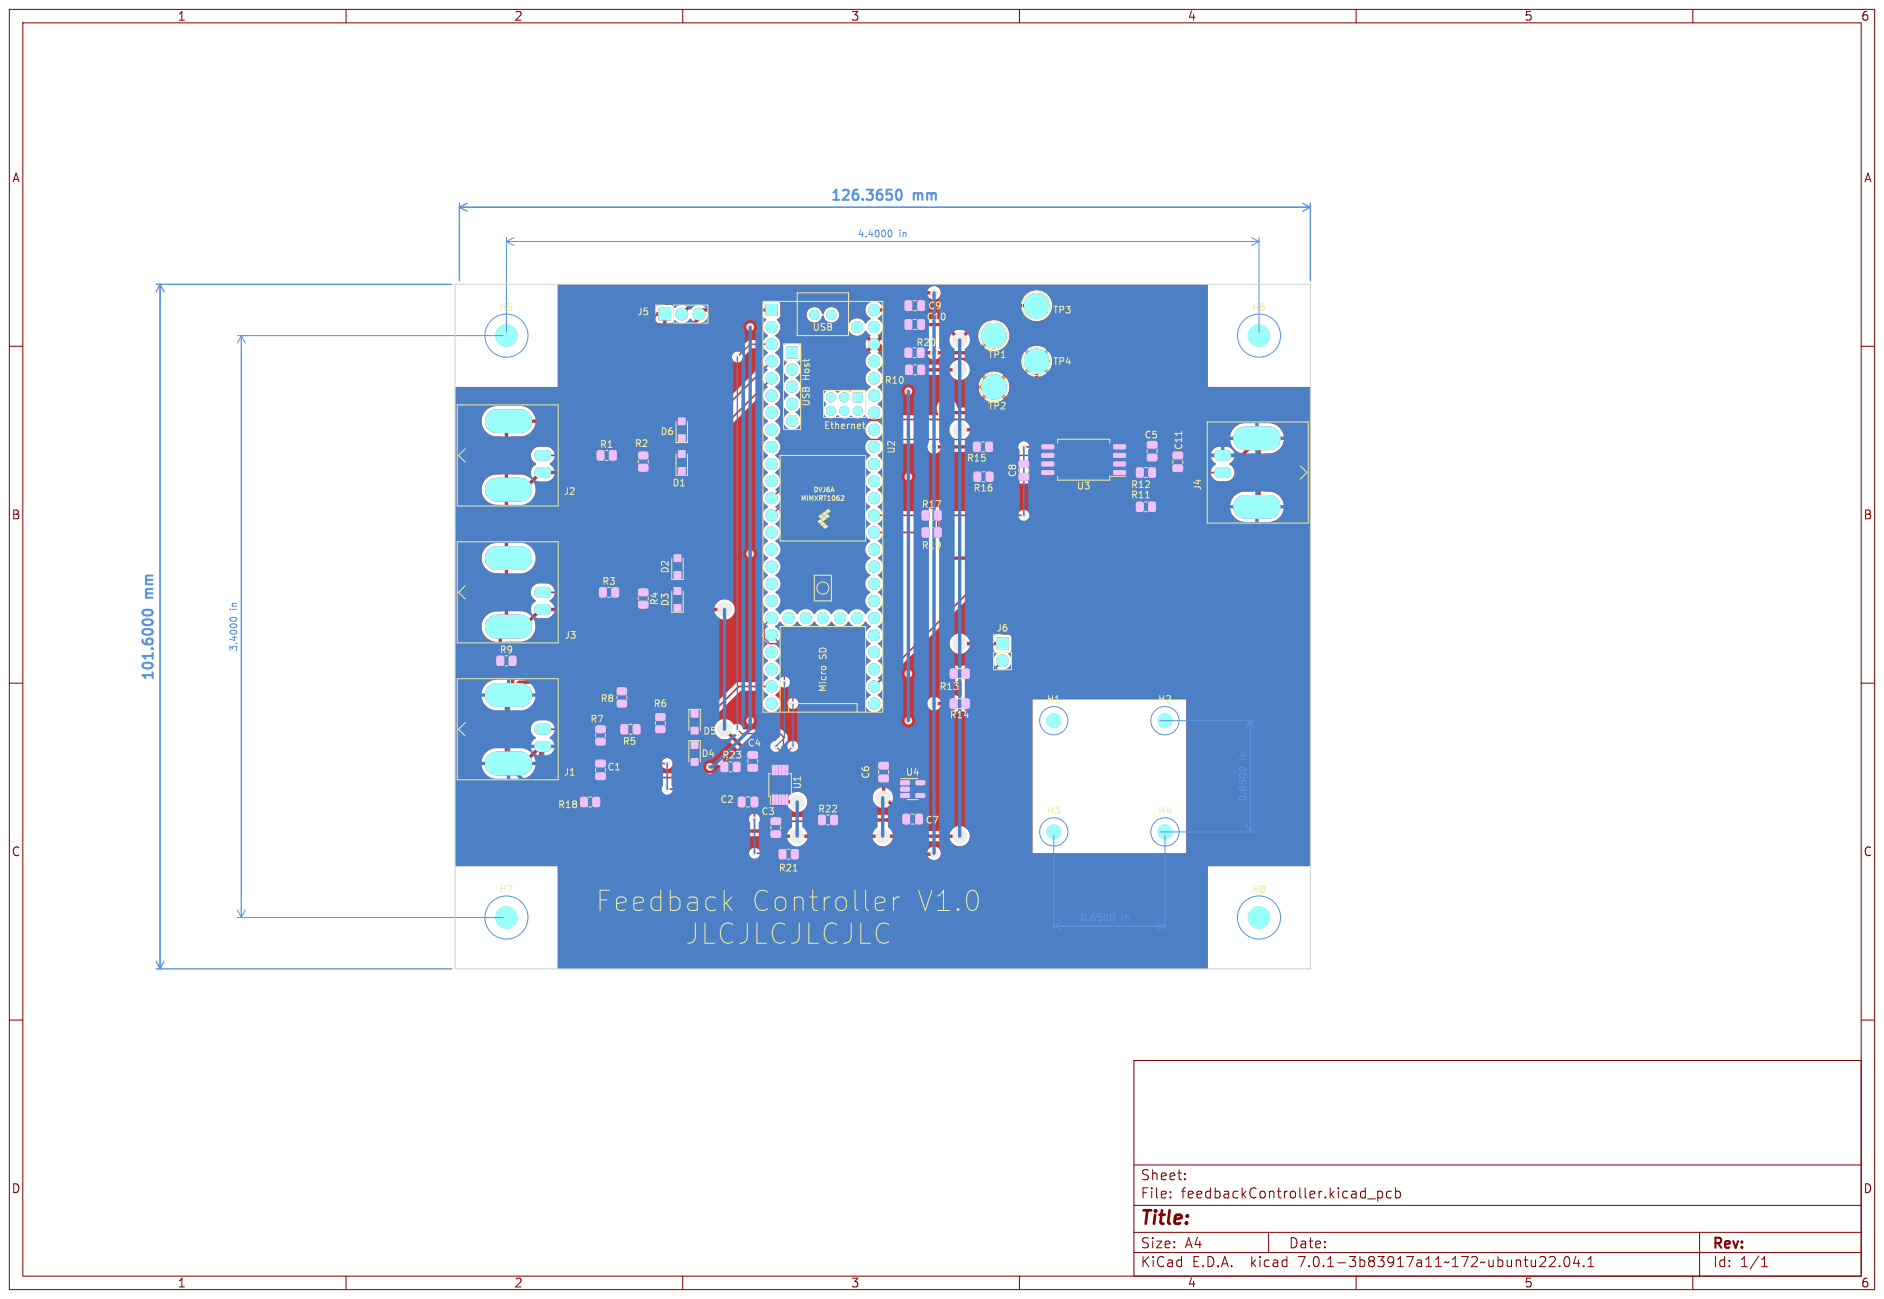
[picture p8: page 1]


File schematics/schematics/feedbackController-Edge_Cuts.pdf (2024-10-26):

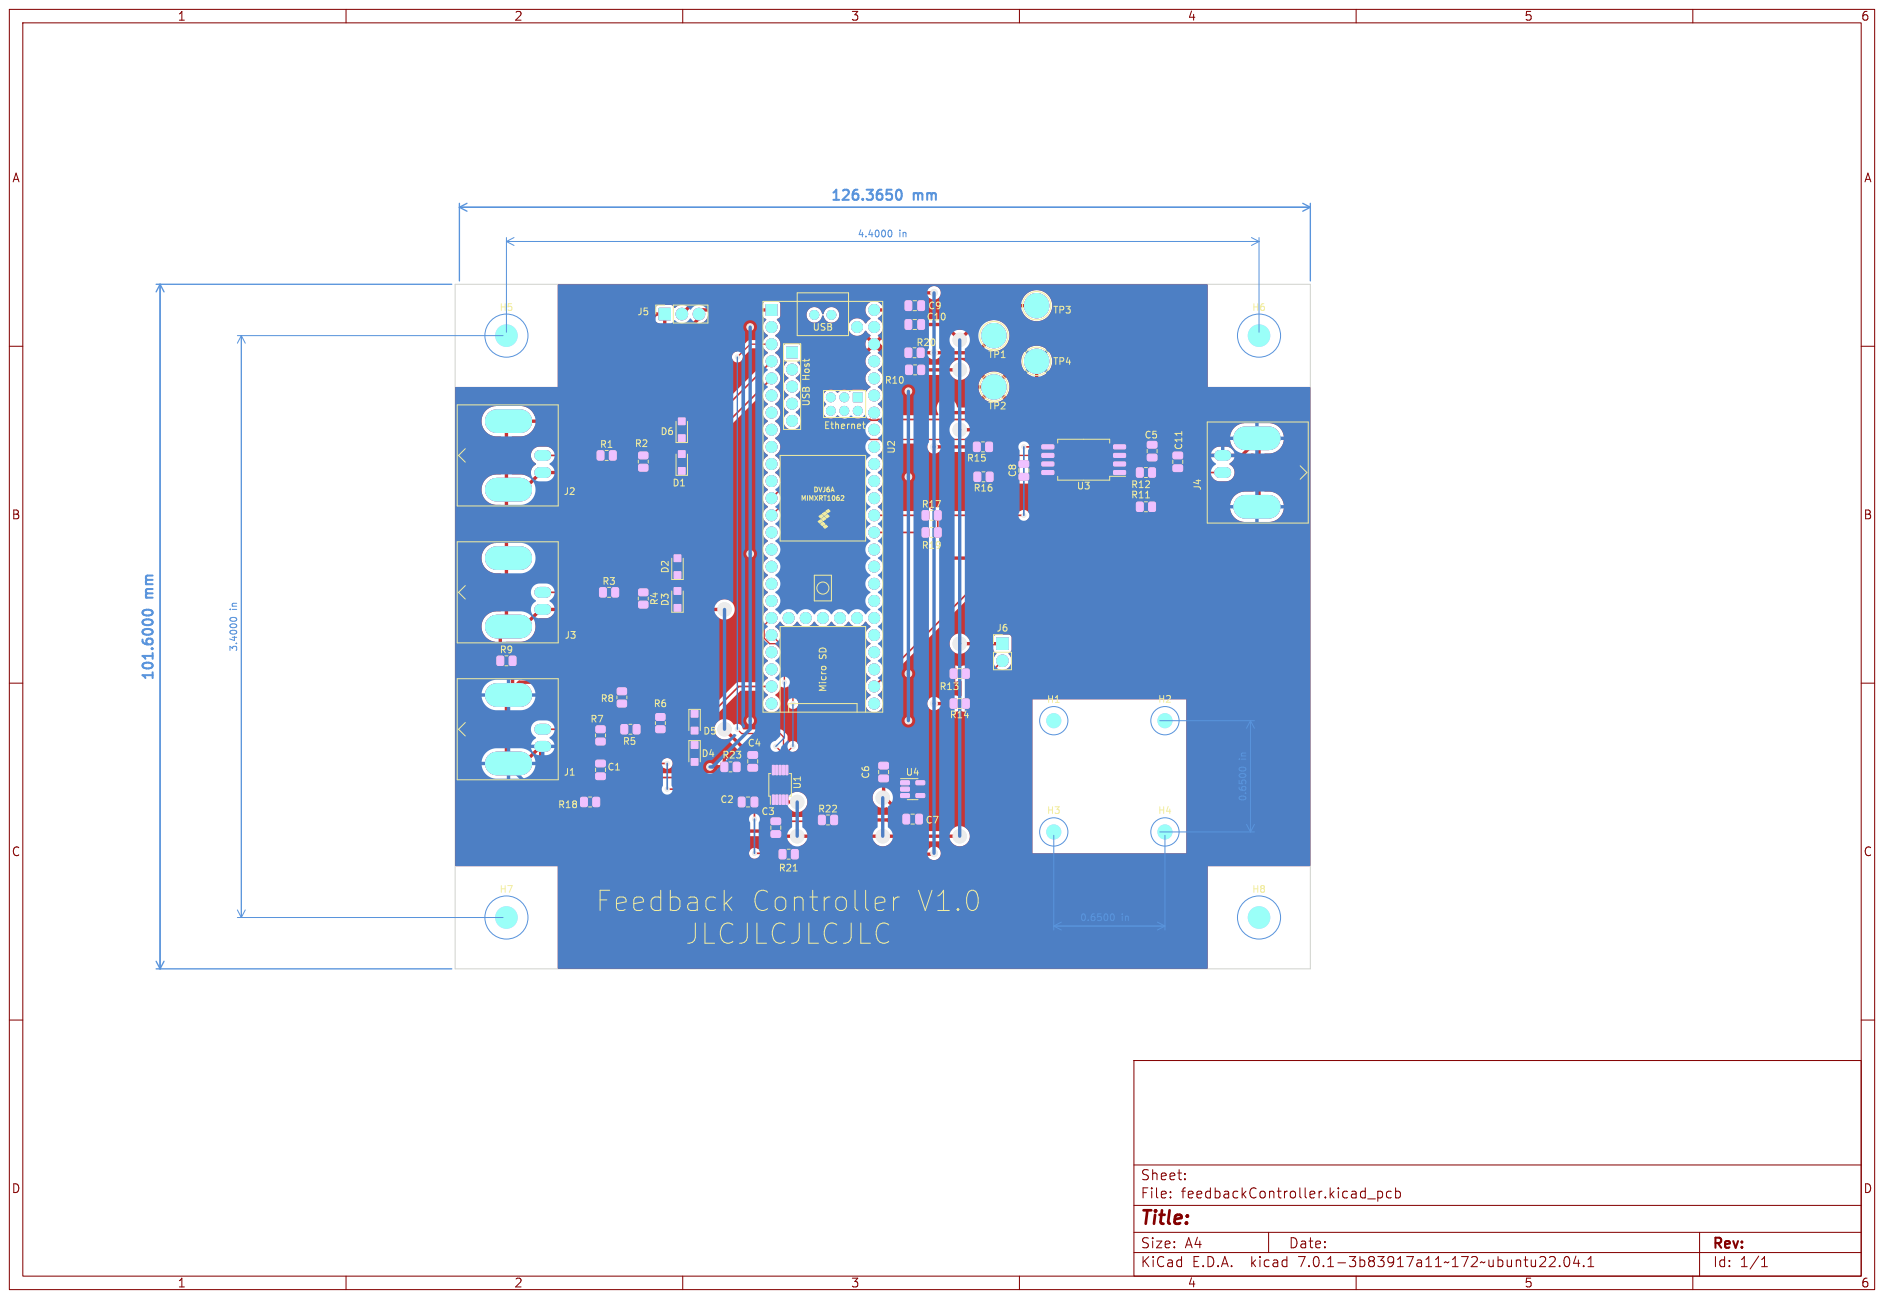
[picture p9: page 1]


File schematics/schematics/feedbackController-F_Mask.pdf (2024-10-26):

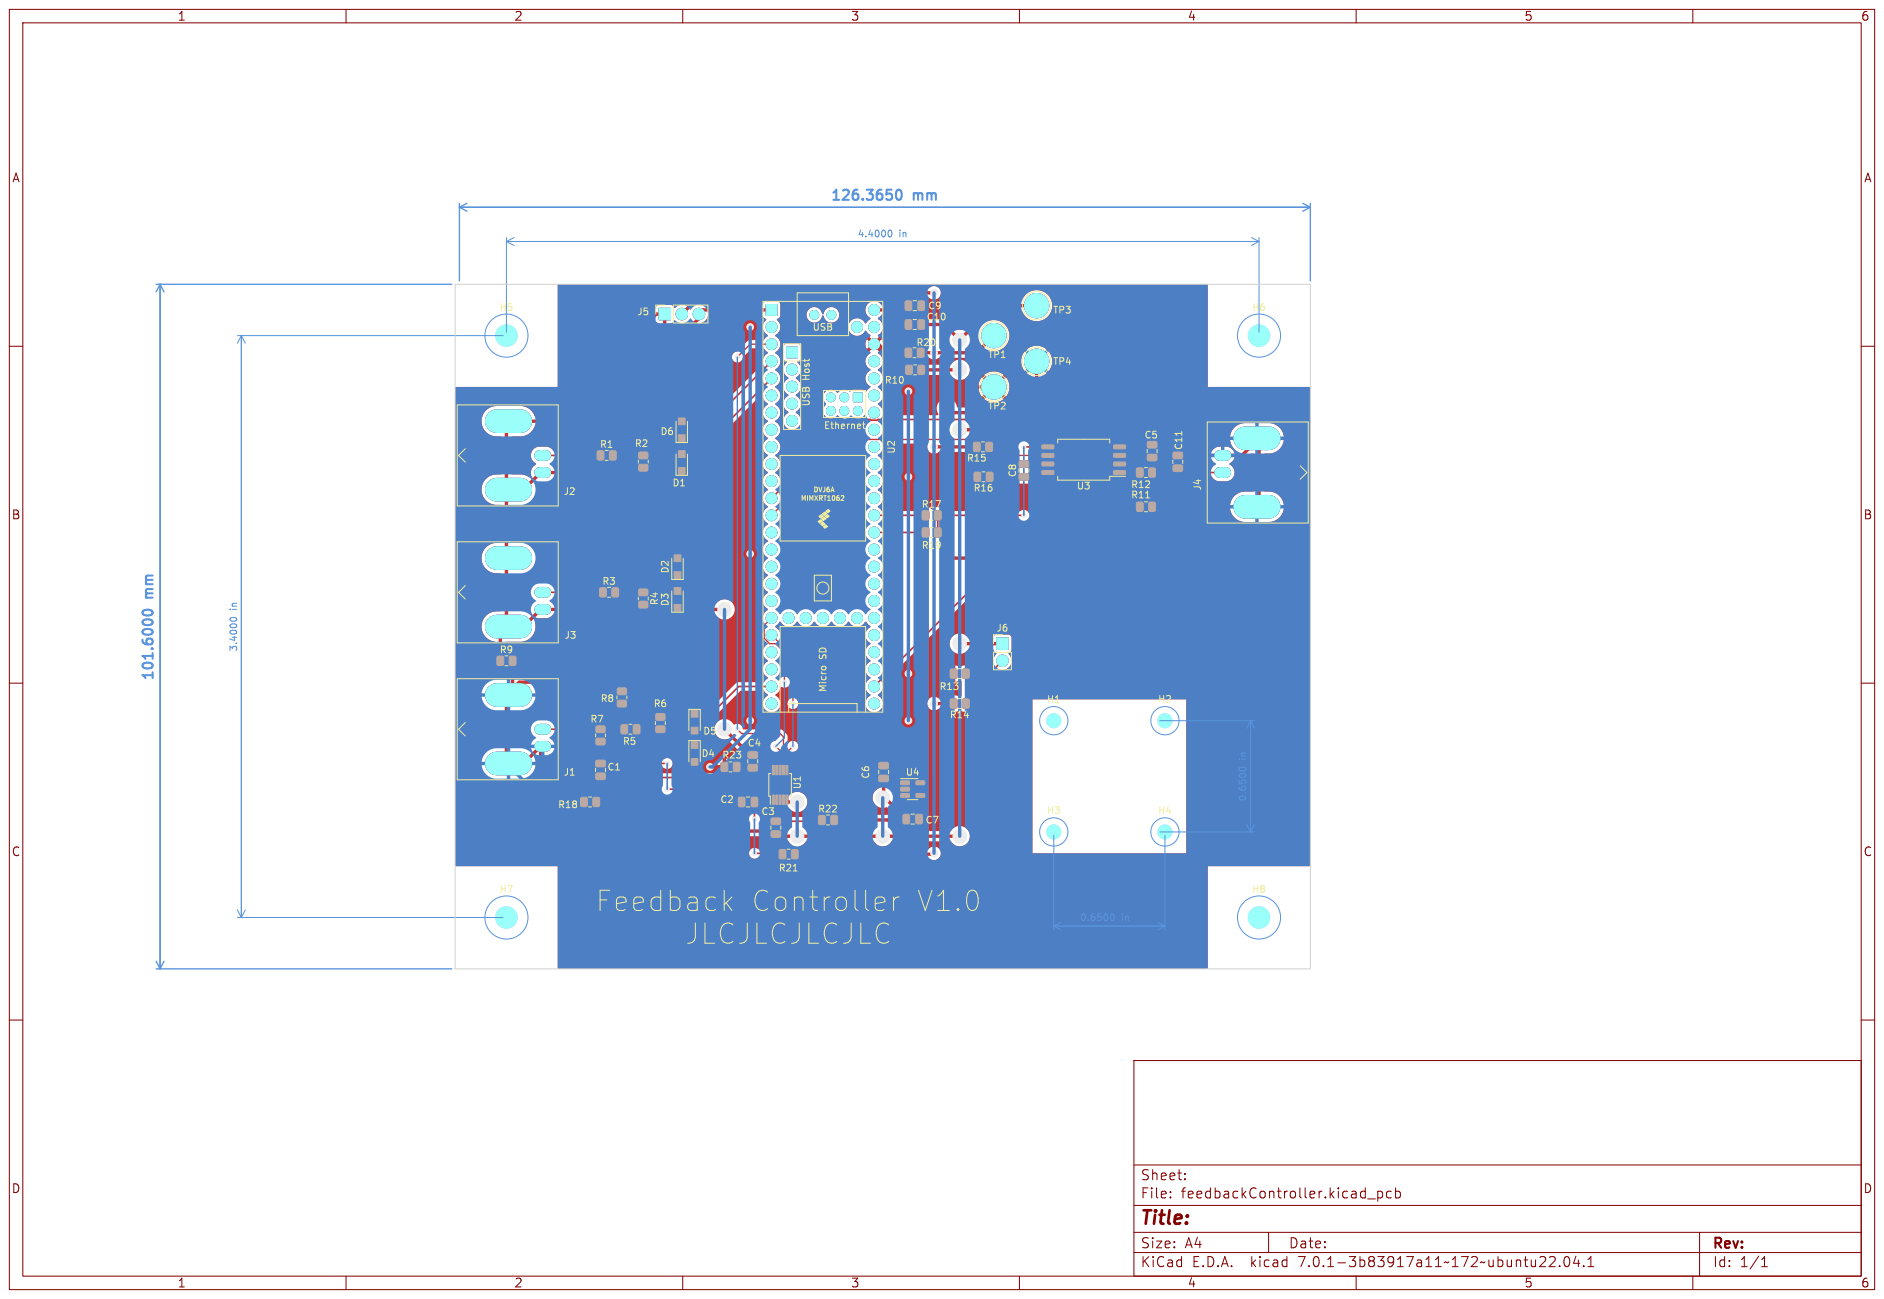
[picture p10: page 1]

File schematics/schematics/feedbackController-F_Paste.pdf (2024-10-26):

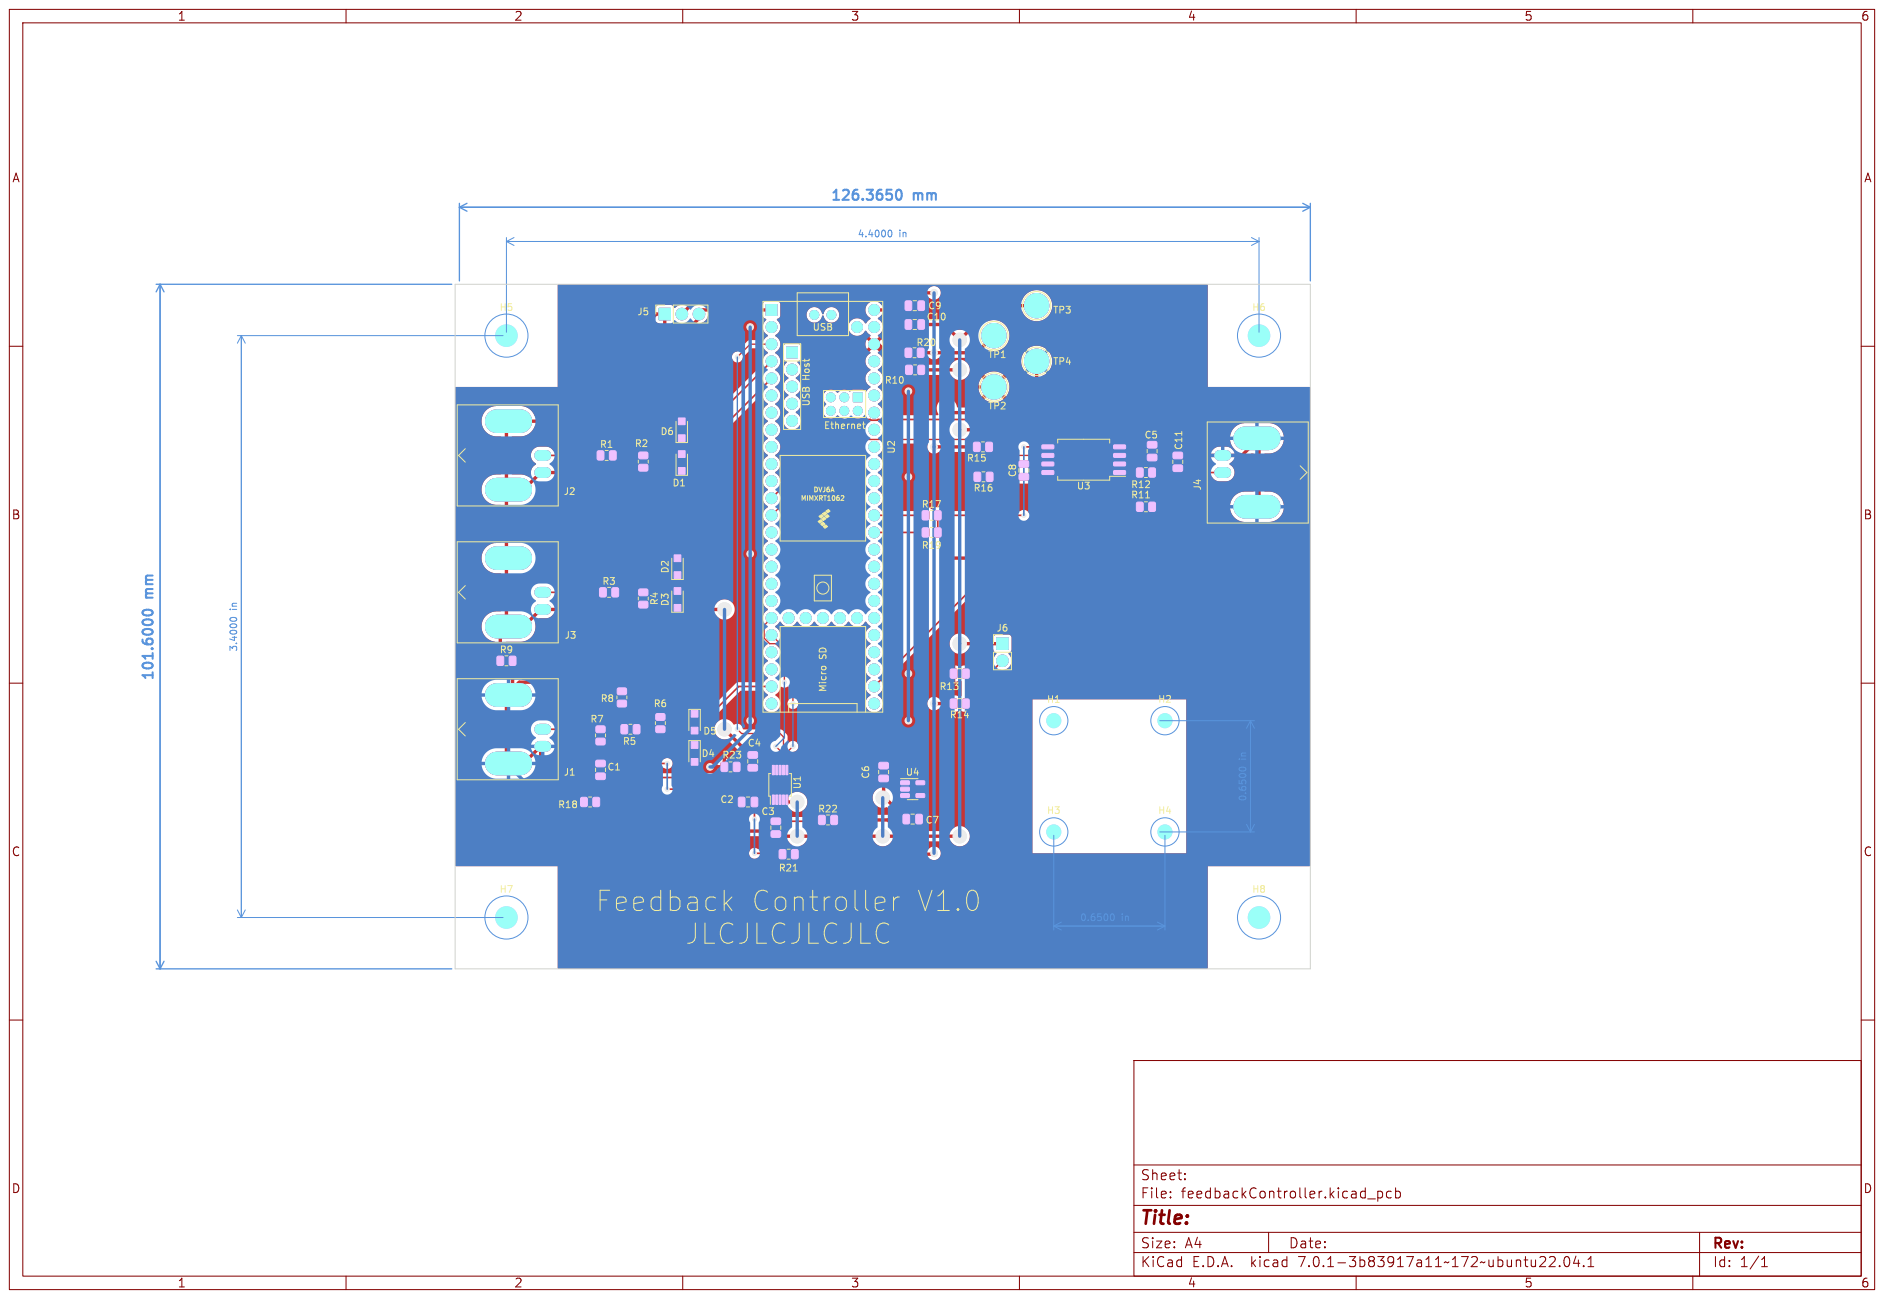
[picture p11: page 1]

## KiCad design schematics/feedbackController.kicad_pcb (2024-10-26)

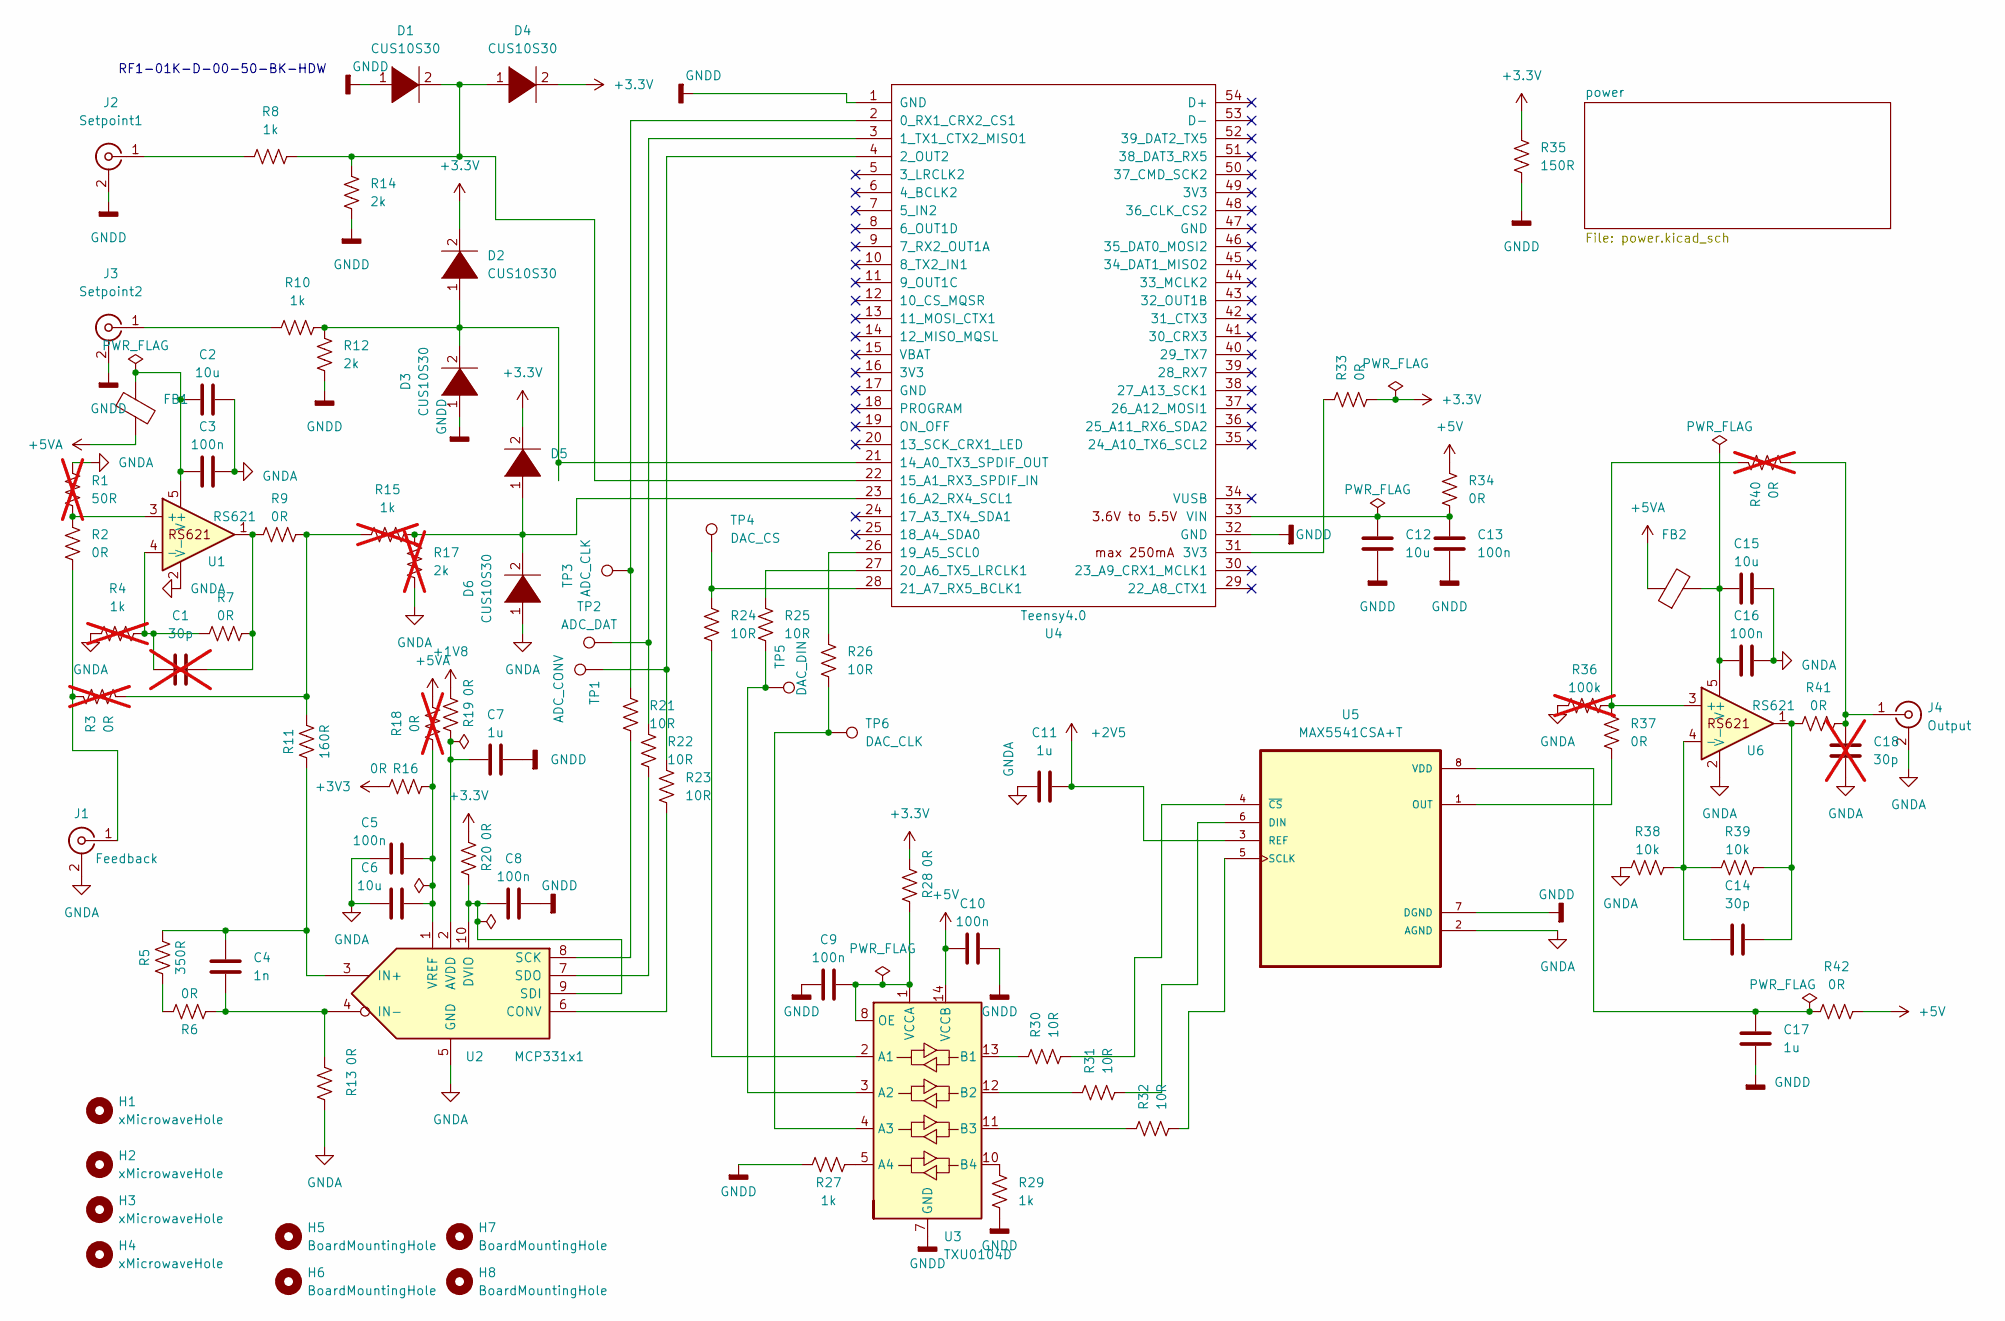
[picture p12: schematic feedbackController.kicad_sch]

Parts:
C1, C18: 30p; C_0805_2012Metric; not fitted
C2, C6, C12, C15: 10u; C_0805_2012Metric
C3, C5, C8, C9, C10, C13, C16: 100n; C_0805_2012Metric
C4: 1n; C_0805_2012Metric
C7, C11, C17: 1u; C_0805_2012Metric
C14: 30p; C_0805_2012Metric
D1, D2, D3, D4, D5, D6: CUS10S30; D_SOD-323_HandSoldering
FB1, FB2: FerriteBead; R_0805_2012Metric_Pad1.20x1.40mm_HandSolder
H1, H2, H3, H4: xMicrowaveHole; MountingHole_2.1mm
H5, H6, H7, H8: BoardMountingHole; MountingHole_3.2mm_M3
J1: Feedback; BNC_Amphenol_B6252HB-NPP3G-50_Horizontal
J2: Setpoint1; BNC_Amphenol_B6252HB-NPP3G-50_Horizontal
J3: Setpoint2; BNC_Amphenol_B6252HB-NPP3G-50_Horizontal
J4: Output; BNC_Amphenol_B6252HB-NPP3G-50_Horizontal
R1: 50R; R_0805_2012Metric; not fitted
R2, R6, R7, R9, R13, R16, R19, R20, R28, R33, R34, R37, R41, R42: 0R; R_0805_2012Metric
R3, R18, R40: 0R; R_0805_2012Metric; not fitted
R4, R15: 1k; R_0805_2012Metric; not fitted
R5: 350R; R_0805_2012Metric
R8, R10, R27, R29: 1k; R_0805_2012Metric
R11: 160R; R_0805_2012Metric
R12, R14: 2k; R_0805_2012Metric
R17: 2k; R_0805_2012Metric; not fitted
R21, R22, R23, R24, R25, R26, R30, R31, R32: 10R; R_0805_2012Metric
R35: 150R; R_0805_2012Metric
R36: 100k; R_0805_2012Metric; not fitted
R38, R39: 10k; R_0805_2012Metric
TP1: ADC_CONV; TestPoint_Loop_D2.50mm_Drill1.0mm
TP2: ADC_DAT; TestPoint_Loop_D2.50mm_Drill1.0mm
TP3: ADC_CLK; TestPoint_Loop_D2.50mm_Drill1.0mm
TP4: DAC_CS; TestPoint_Loop_D2.50mm_Drill1.0mm
TP5: DAC_DIN; TestPoint_Loop_D2.50mm_Drill1.0mm
TP6: DAC_CLK; TestPoint_Loop_D2.50mm_Drill1.0mm
U1, U6: RS621; SOT-23-5_HandSoldering
U2: MCP331x1; MSOP-10_3x3mm_P0.5mm
U3: TXU0104D; SOIC-14_3.9x8.7mm_P1.27mm
U4: Teensy4.0; Teensy40
U5: MAX5541CSA+T; SOIC-8_3.9x4.9mm_P1.27mm

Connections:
+1V8: R19.2; also elsewhere on the board
+2V5: C11.2, U5.3 (REF); also elsewhere on the board
+3.3V: D2.2 (A), D4.2 (A), D5.2 (A), R20.2, R28.2, R33.1, R35.1; also elsewhere on the board
+3V3: R16.2; also elsewhere on the board
+5V: C10.1, R34.2, R42.2, U3.14 (VCCB); also elsewhere on the board
+5VA: FB1.2, FB2.1, R18.2; also elsewhere on the board
GNDA: C2.2, C3.2, C5.1, C6.1, C11.1, C15.2, C16.2, C18.2, D6.1 (K), J1.2 (Ext), J4.2 (Ext), R1.1, R4.1, R13.1, R17.2, R36.1, R38.1, U1.2 (V-), U2.5 (GND), U5.2 (AGND), U6.2 (V-); also elsewhere on the board
GNDD: C7.2, C8.2, C9.1, C10.2, C12.2, C13.2, C17.2, D1.1 (K), D3.1 (K), J2.2 (Ext), J3.2 (Ext), R12.2, R14.2, R27.1, R29.2, R35.2, U3.7 (GND), U4.1 (GND), U4.32 (GND), U5.7 (DGND); also elsewhere on the board
unnamed: C1.2, R7.2, R9.1, U1.1
unnamed: C14.2, R39.2, R41.1, U6.1
unnamed: D1.2 (A), D4.1 (K), R8.2, R14.1, U4.22 (15_A1_RX3_SPDIF_IN)
unnamed: D2.1 (K), D3.2 (A), R10.2, R12.1, U4.21 (14_A0_TX3_SPDIF_OUT)
unnamed: D5.1 (K), D6.2 (A), R15.2, R17.1, U4.23 (16_A2_RX4_SCL1)
unnamed: J1.1 (In), R2.2, R3.1
unnamed: J2.1 (In), R8.1
unnamed: J3.1 (In), R10.1
unnamed: C18.1, J4.1 (In), R40.2, R41.2
unnamed: R5.1, R6.2
unnamed: R3.2, R9.2, R11.2, R15.1
unnamed: R33.2, U4.31 (3V3)
unnamed: R1.2, R2.1, U1.3 (+)
unnamed: C1.1, R4.2, R7.1, U1.4 (-)
unnamed: C2.1, C3.1, FB1.1, U1.5 (V+)
unnamed: C7.1, R19.1, U2.2 (AVDD)
unnamed: R23.1, U2.6 (CONV)
unnamed: C8.1, R20.1, U2.9 (SDI), U2.10 (DVIO)
unnamed: C4.1, R5.2, R11.1, U2.3 (IN+)
unnamed: C4.2, R6.1, R13.2, U2.4 (IN-)
unnamed: R21.1, U2.8 (SCK)
unnamed: R22.1, U2.7 (SDO)
unnamed: C5.2, C6.2, R16.1, R18.1, U2.1 (VREF)
unnamed: R24.1, U3.2 (A1)
unnamed: R25.1, TP5.1, U3.3 (A2)
unnamed: R26.1, TP6.1, U3.4 (A3)
unnamed: R27.2, U3.5 (A4)
unnamed: R30.2, U3.13 (B1)
unnamed: R31.2, U3.12 (B2)
unnamed: R32.2, U3.11 (B3)
unnamed: R29.1, U3.10 (B4)
unnamed: C9.2, R28.1, U3.1 (VCCA), U3.8 (OE)
unnamed: R21.2, TP3.1, U4.2 (0_RX1_CRX2_CS1)
unnamed: R22.2, TP2.1, U4.3 (1_TX1_CTX2_MISO1)
unnamed: R23.2, TP1.1, U4.4 (2_OUT2)
unnamed: R26.2, U4.26 (19_A5_SCL0)
unnamed: R25.2, U4.27 (20_A6_TX5_LRCLK1)
unnamed: R24.2, TP4.1, U4.28 (21_A7_RX5_BCLK1)
unnamed: C12.1, C13.1, R34.1, U4.33 (VIN)
unnamed: R31.1, U5.6 (DIN)
unnamed: R37.1, U5.1 (OUT)
unnamed: R32.1, U5.5 (SCLK)
unnamed: C17.1, R42.1, U5.8 (VDD)
unnamed: R30.1, U5.4 (~CS)
unnamed: R36.2, R37.2, R40.1, U6.3 (+)
unnamed: C14.1, R38.2, R39.1, U6.4 (-)
unnamed: C15.1, C16.1, FB2.2, U6.5 (V+)

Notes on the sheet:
RF1-01K-D-00-50-BK-HDW

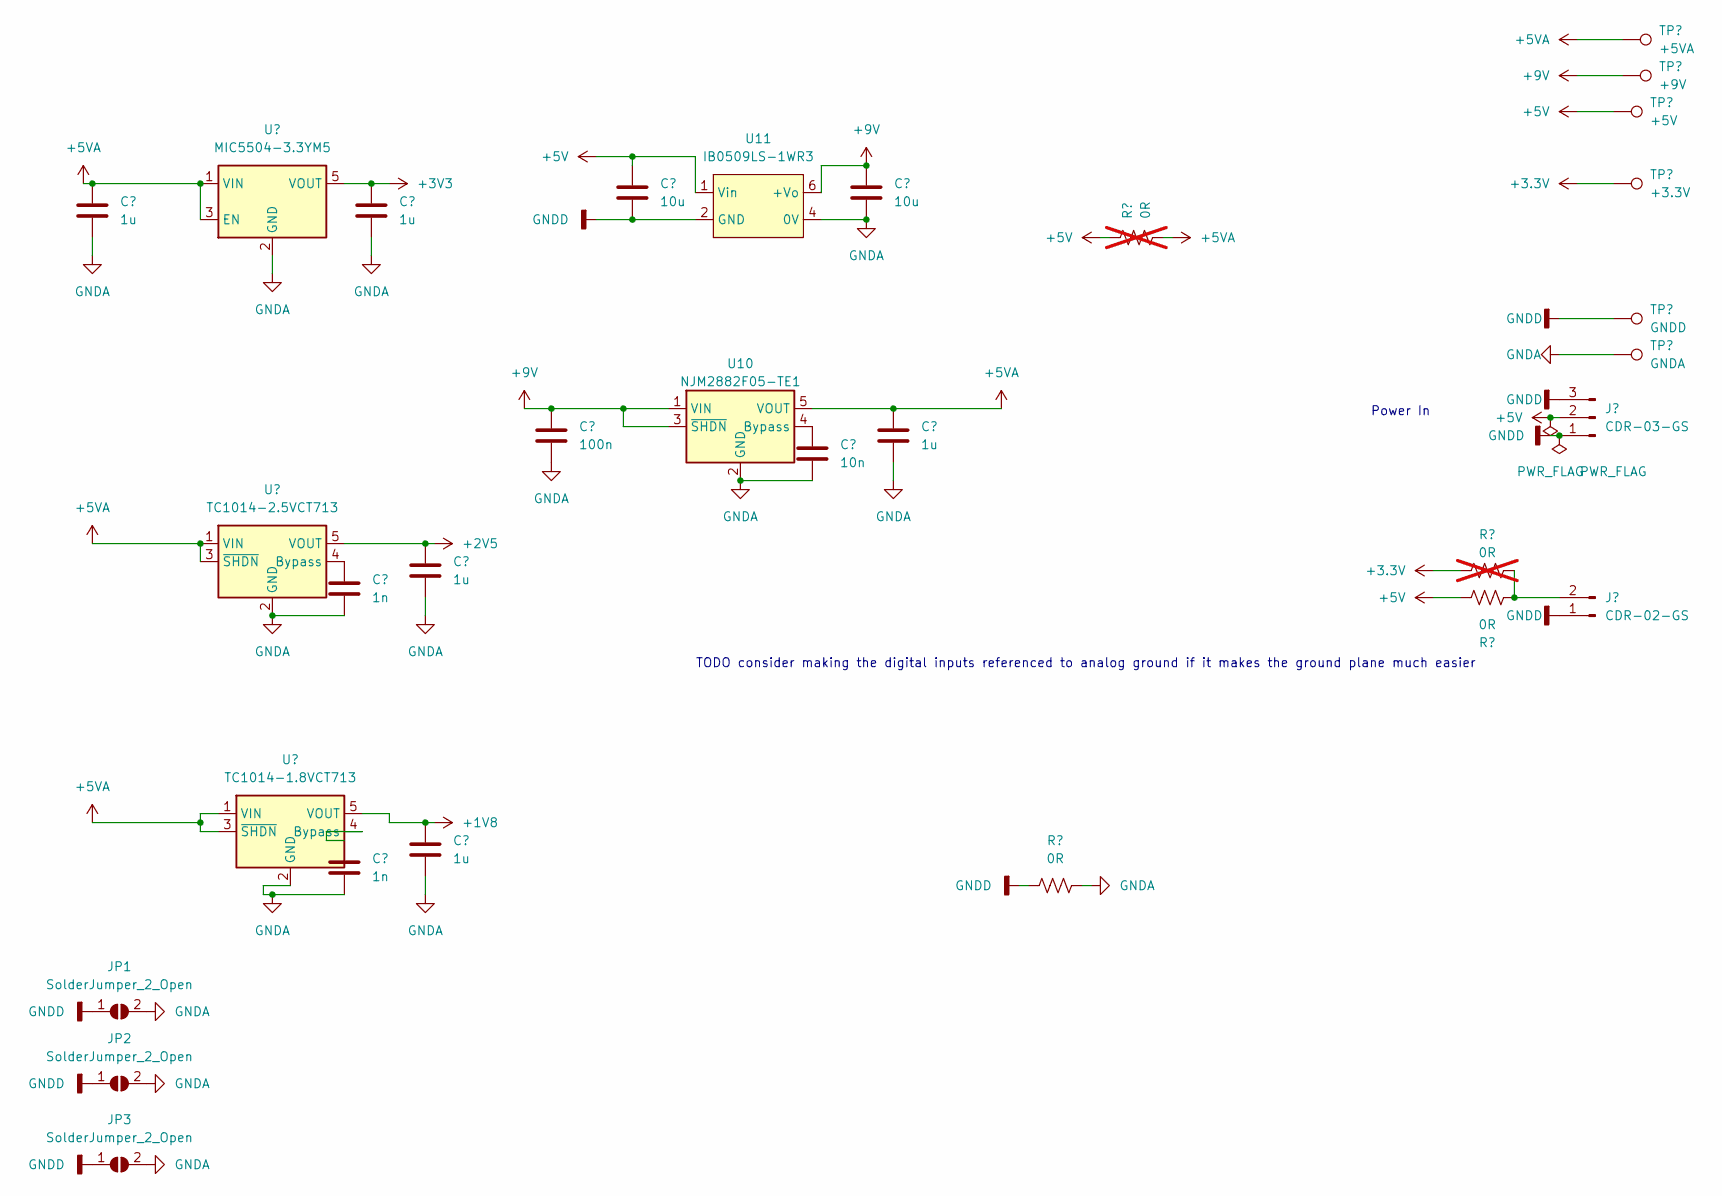
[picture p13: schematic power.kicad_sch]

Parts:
C19, C22, C23, C24, C29: 1u; C_0805_2012Metric
C20, C21: 1n; C_0805_2012Metric
C25: 100n; C_0805_2012Metric
C26, C28: 10u; C_0805_2012Metric
C27: 10n; C_0805_2012Metric
J5: CDR-03-GS; PinSocket_1x03_P2.54mm_Vertical
J6: CDR-02-GS; PinHeader_1x02_P2.54mm_Vertical
JP1, JP2, JP3: SolderJumper_2_Open; SolderJumper-2_P1.3mm_Open_Pad1.0x1.5mm
R43, R46: 0R; R_0805_2012Metric
R44, R45: 0R; R_0805_2012Metric; not fitted
TP7: +5V; TestPoint_Loop_D2.50mm_Drill1.0mm
TP8: +3.3V; TestPoint_Loop_D2.50mm_Drill1.0mm
TP9: GNDD; TestPoint_Loop_D2.50mm_Drill1.0mm
TP10: GNDA; TestPoint_Loop_D2.50mm_Drill1.0mm
TP11: +5VA; TestPoint_Loop_D2.50mm_Drill1.0mm
TP12: +9V; TestPoint_Loop_D2.50mm_Drill1.0mm
U7: MIC5504-3.3YM5; SOT-23-5
U8: TC1014-2.5VCT713; SOT-23-5
U9: TC1014-1.8VCT713; SOT-23-5
U10: NJM2882F05-TE1; SOT-23-5_HandSoldering
U11: IB0509LS-1WR3; IB05_LS-1WR3

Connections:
+1V8: C24.1, U9.5 (VOUT); also elsewhere on the board
+2V5: C23.1, U8.5 (VOUT); also elsewhere on the board
+3.3V: R45.2, TP8.1; also elsewhere on the board
+3V3: C22.1, U7.5 (VOUT); also elsewhere on the board
+5V: C26.1, J5.2, R44.2, R46.2, TP7.1, U11.1 (Vin); also elsewhere on the board
+5VA: C19.1, C29.1, R44.1, TP11.1, U7.1 (VIN), U7.3 (EN), U8.1 (VIN), U8.3 (~SHDN), U9.1 (VIN), U9.3 (~SHDN), U10.5 (VOUT); also elsewhere on the board
+9V: C25.1, C28.1, TP12.1, U10.1 (VIN), U10.3 (~SHDN), U11.6 (+Vo)
GNDA: C19.2, C20.2, C21.2, C22.2, C23.2, C24.2, C25.2, C27.2, C28.2, C29.2, JP1.2 (B), JP2.2 (B), JP3.2 (B), R43.2, TP10.1, U7.2 (GND), U8.2 (GND), U9.2 (GND), U10.2 (GND), U11.4 (0V); also elsewhere on the board
GNDD: C26.2, J5.1, J5.3, J6.1, JP1.1 (A), JP2.1 (A), JP3.1 (A), R43.1, TP9.1, U11.2 (GND); also elsewhere on the board
unnamed: J6.2, R45.1, R46.1
unnamed: C20.1, U8.4 (Bypass)
unnamed: C21.1, U9.4 (Bypass)
unnamed: C27.1, U10.4 (Bypass)

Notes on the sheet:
TODO consider making the digital inputs referenced to analog ground if it makes the ground plane much easier
Power In

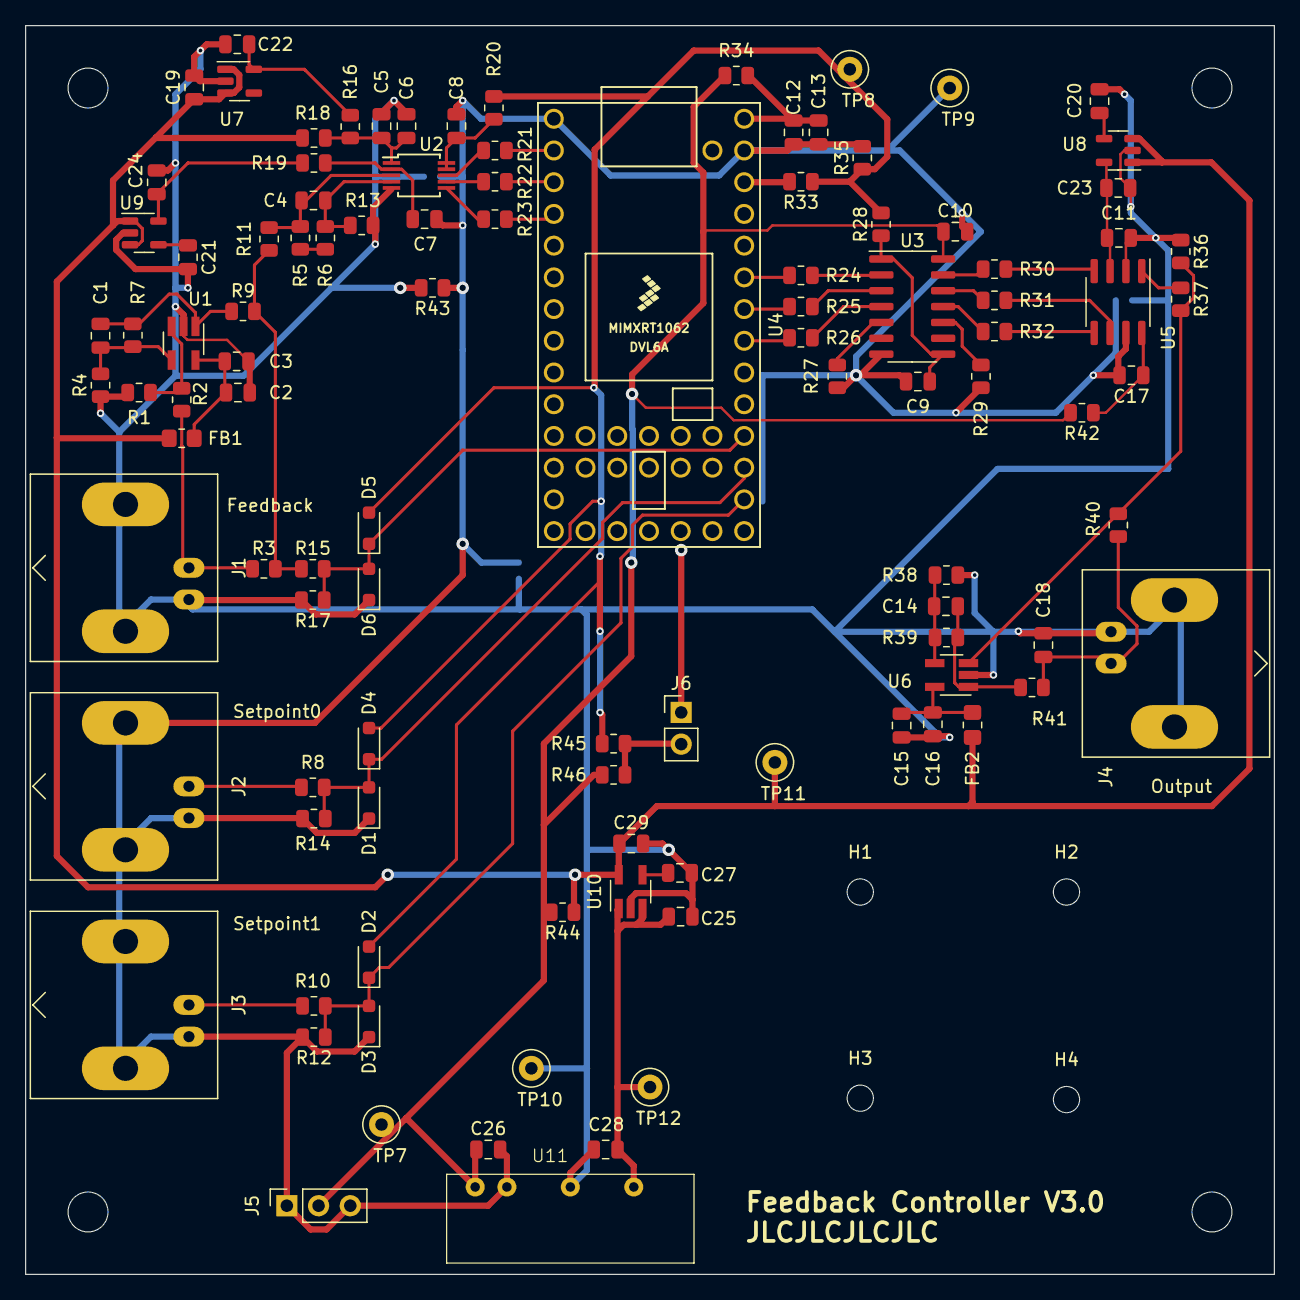
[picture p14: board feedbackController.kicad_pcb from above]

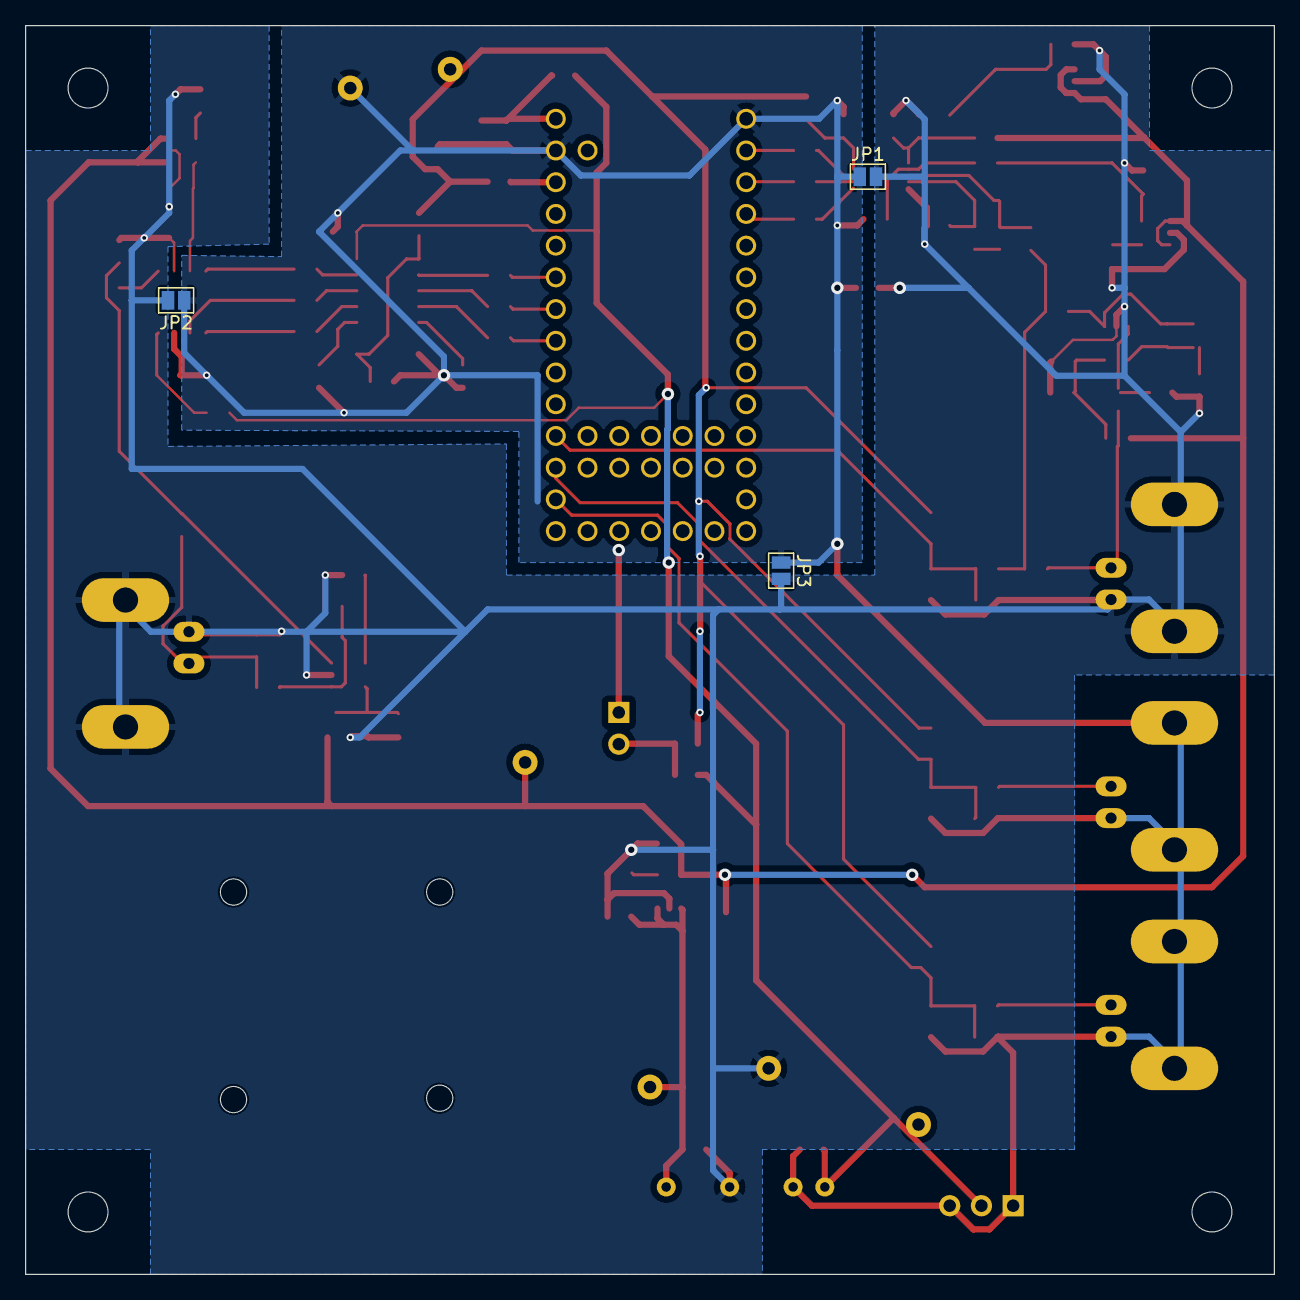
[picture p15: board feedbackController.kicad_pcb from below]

Board: 2 copper layers, 100.0 x 100.0 mm, 117 parts (3 on the bottom side), 60 nets.

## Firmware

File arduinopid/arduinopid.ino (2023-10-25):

/*
 * This is PID feedback control code intended to be used with the Teensy 3.2: 
 * https://www.pjrc.com/teensy/teensy31.html
 * Its pins are here:
 * https://www.pjrc.com/teensy/pinout.html
 * And its schematic is here:
 * https://www.pjrc.com/teensy/schematic.html
 * 
 * Most of the PID feedback control code is from here: https://github.com/mike-matera/FastPID/blob/master/src/FastPID.cpp
 * 
 * look here for code to speed up ADC: https://github.com/pedvide/ADC/blob/master/examples/analogContinuousRead/analogContinuousRead.ino
 * 
 * If using digital control code, use pyserial to adjust setpoint: https://anaconda.org/anaconda/pyserial
 */

/*
 * 
 * TODO print warning and sets flag if output has railed (is set equal to max output) when setpoint has not railed
 * 
 */

 /*
  * TODO
  - -add optional buffer that stores output values to be printed at a later date (ro=1, ro=0, ro?)
  * -clean up code, split into multiple files
  * -look through previous todos
  * -(MAYBE) use one digital input to turn feedback control on/off, and use the other as a setpoint
  */

#include "arduinopid.h"
#include <EEPROM.h>     //for permanently saving settings
#include "CircularBuffer.h" //prepackaged Circular Buffer

//pid feedback control parameters

#if FEEDFORWARD
float kp=.005, ki=1000, kd=0; //good starting point for feedforward
#else
float kp=0.01, ki=100, kd=0; //good starting point for non-feedforward
#endif
/*float kp=1;
float ki=kp*SAMPLE_RATE_HZ;
float kd=0;*/
//this is also the setpoint if digital input is low
uint32_t loopRateHz = DEFAULT_SAMPLE_RATE_HZ;
#define loopPeriodUs (uint32_t)(1000000/loopRateHz)
uint16_t setpoint = ADC_VOLTS2BITS(DEFAULT_SETPOINT); //default setpoint (voltage it reads)

#if INPUT_MODE == DIGITAL_INPUT
	uint16_t setpoints[INPUT_STATES];	//default low digital setpoint
	uint8_t statenumber = 0;
#endif
uint8_t readaveragespower = READDAVERAGESPOWER;	//number of times to average the input (hardware)


#if LIMITED_SETPOINT
	uint16_t minsetpoint = ADC_VOLTS2BITS(0.05);
	uint16_t maxsetpoint = ADC_VOLTS2BITS(.95*ADC_VREF);
	uint16_t minoutput = 0;
	uint16_t maxoutput = MAX_OUTPUT;

	//TODO setOutputRange if not feedforward
#endif


//things that only need to be defined if feedback control is active
#ifdef SERIAL_BAUD
	char instring[INSTRING_LENGTH];   //input string
    char outstring[255];
	uint8_t inind = 0;
	bool serialActive = false;      //serial active flag
	uint8_t printout = 0;        //if true, print feedback stats
	volatile bool readSerial = true;  //read serial flag
#endif

volatile bool pidcalc = true; //flag saying to perform feedback control calc
volatile bool pidactive = true;      //flag saying "pid control is active"

#if FEEDFORWARD
    const uint32_t FEEDFORWARD_ARRAY_LENGTH = (MAX_INPUT+1); //want to have a value for each and every setpoint
    const uint32_t FF_CALIB_ARRAY_LENGTH = (FEEDFORWARD_ARRAY_LENGTH/16);//1024//length of array used to generate the abovearray
    #define ffCalibOutput(x) (int)((x*((1 << DAC_BITS) - 1))/(FF_CALIB_ARRAY_LENGTH - 1))
    #define CALIBRATION_AVERAGES_POWER 8
	#define CALIBRATION_SETTLE_DELAY_US 10
	#define CALIBRATION_PRE_SETTLE_DELAY_US 10000
    uint16_t feedforward[FEEDFORWARD_ARRAY_LENGTH];
    uint16_t ffCalib[FF_CALIB_ARRAY_LENGTH];
#endif

#if RECORD_INPUT
	typedef enum{
		LOG_OFF, //don't log output
		LOG_SINGLE, //log until full
		LOG_CONTINUOUS	//continue logging, overwriting old data
	}LogState;
	const uint32_t INPUT_LOG_SIZE = 150000/2;
	CircularBuffer<uint16_t, INPUT_LOG_SIZE> inputLog;
	CircularBuffer<uint16_t, INPUT_LOG_SIZE> outputLog;
	LogState logstate = LOG_OFF;
#endif

#if INPUT_MODE == ANALOG_INPUT
	#define readAnalogReference() analogRead(PIN_REFERENCE) << (ADC_BITS - ANALOGREFERENCERESOLUTION);
#endif

IntervalTimer pidTimer; //used for timing the pid feedback loop
IntervalTimer readTimer; //used for timing the serial read code

FastPID myPID(kp, ki, kd, loopRateHz, DAC_BITS, SIGNED_OUTPUT); //feedback control object

//private functions
#ifdef SERIAL_BAUD
void updateparams(char* string);  //updates parameters given string
#endif
void setpidcalc();          //sets pid calc flag (ISR)
void setreadserial();       //sets read serial flag (ISR)

#if FEEDFORWARD
void getFeedforwardReadings(uint16_t* readings);
void calibrateFeedforward(uint16_t* readings);
#endif

#if SAVE_DATA //TODO also save read averages
    const uint16_t KI_EEPROM_ADDRESS=0, KP_EEPROM_ADDRESS=4, KD_EEPROM_ADDRESS=8;
    const uint16_t LR_EEPROM_ADDRESS=20;
    void savePID(float ki, float kp, float kd, uint32_t looprate);
    void loadPID(float& ki, float& kp, float& kd, uint32_t& looprate);
    #if LIMITED_SETPOINT
    const uint16_t MINSP_EEPROM_ADDRESS = 12, MAXSP_EEPROM_ADDRESS = 14, MINOP_EEPROM_ADDRESS = 16, MAXOP_EEPROM_ADDRESS = 18;
    void saveLimits(uint16_t minsetpoint, uint16_t maxsetpoint, uint16_t minoutput, uint16_t maxoutput);
    void loadLimits(uint16_t& minsetpoint, uint16_t& maxsetpoint, uint16_t& minoutput, uint16_t& maxoutput);
    #endif
    #if FEEDFORWARD
    const uint16_t FFDATA_EEPROM_ADDRESS = 512;
    void saveFFdata(uint16_t* readings);
    void loadFFdata(uint16_t* readings);
    #endif

void saveEverything()
{
    savePID(ki, kp, kd, loopRateHz);
    #if LIMITED_SETPOINT
        saveLimits(minsetpoint, maxsetpoint, minoutput, maxoutput);
    #endif
    #if FEEDFORWARD
    saveFFdata(ffCalib);
    #endif
}

void loadEverything()
{
    loadPID(ki, kp, kd, loopRateHz);
    #if LIMITED_SETPOINT
    //    loadLimits(minsetpoint, maxsetpoint, minoutput, maxoutput);
    #endif
    #if FEEDFORWARD
    loadFFdata(ffCalib);
    #endif
}
    
#endif


void setup()
{
	//sets pin states
#if INPUT_MODE == DIGITAL_INPUT
	pinMode(PIN_REFERENCE0, INPUT);
	pinMode(PIN_REFERENCE1, INPUT);
#elif INPUT_MODE == ANALOG_INPUT
	pinMode(PIN_REFERENCE, INPUT);
	analogReadAveraging(ANALOGREADAVERAGES);
	analogReadResolution(ANALOGREFERENCERESOLUTION);
#endif
    initADC();
    initDAC();
	
	//sets up serial
	#ifdef SERIAL_BAUD

		Serial.begin(SERIAL_BAUD);
		serialActive = true;
		while(myPID.err()) 
		{
            if(Serial)
            {
		        Serial.println("There is a configuration error!");
            }
            delay(1000);
		}

		Serial.println("PID Begin");
		readTimer.begin(setreadserial, READ_PERIOD_MS*1000);
	#endif

	//begins pid feedback loop timer
	pidTimer.begin(setpidcalc, loopPeriodUs);

#if SAVE_DATA
    loadEverything();
#endif

#if FEEDFORWARD && !SAVE_DATA
    getFeedforwardReadings(ffCalib);
    calibrateFeedforward(ffCalib);   
#endif

	myPID.clear(); 
	myPID.configure(kp, ki, kd, loopRateHz, DAC_BITS, SIGNED_OUTPUT);
	myPID.clear(); 


	Serial.println(PARAM_MULT);
}

//feedback control variables 
int32_t feedback = 0;
int32_t out = 0;
int32_t sp = 0;

uint64_t loopTime;
//main loop
void loop()
{ 
	#if RECORD_INPUT
		bool loggedin = false;
		int32_t prevout = out;
	#endif
    bool skipcalc = false; //set to true if the PID calc should be skipped (if pid setpoint is out of limits)
	//run feedback control loop
    #if TIME_FEEDBACK_LOOP
        elapsedMicros timeSinceLoopStart;
		//uint64_t tstart = micros();
		//uint64_t tend = 0;
    #endif
	if(pidcalc)
	{
		pidcalc = false; //resets flag
		#if FEEDFORWARD
			bool onlyff = false;
		#endif
		if(pidactive) //only run if pid is active
		{
			#if INPUT_MODE == ANALOG_INPUT
				sp = readAnalogReference();	
                setpoint = sp;		
			#elif INPUT_MODE == DIGITAL_INPUT
				statenumber = digitalReadFast(PIN_REFERENCE1) << 1 | digitalReadFast(PIN_REFERENCE0);
				int32_t oldsp = sp;
				sp = setpoints[statenumber];
				setpoint = sp;
				bool changedstate = sp != oldsp;


                #if FEEDFORWARD //skip feedback calculation on first step after changing state
                    if(changedstate)
                    {
                        onlyff = true;
                    }
				#endif
			#else
				sp = setpoint;
			#endif


            #if LIMITED_SETPOINT //TODO look into using "clear" here
                if(sp < minsetpoint)
                {
                    #if NEGATIVE_OUTPUT
                    out = maxoutput;
                    #else
                    out = minoutput;
                    #endif
                    skipcalc = true;

					#if ! FEEDFORWARD && CLEAR_INTEGRAL_WHEN_RAILED
						myPID.clear(); //reduces overshoot
					#endif
                    
                }
                else if(sp > maxsetpoint)
                {
                    #if NEGATIVE_OUTPUT
                    out = minoutput;
                    #else
                    out = maxoutput;
                    #endif
                    skipcalc = true;

					#if ! FEEDFORWARD
						myPID.clear(); //reduces overshoot
					#endif
                }
            #endif
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

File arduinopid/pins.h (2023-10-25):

#ifndef PINS
#define PINS

typedef enum{
	REV_V0,
	REV_V2,
	REV_V3
} Board_Rev;

#define BOARD_REV REV_V3

#if (BOARD_REV == REV_V3)
    #define PIN_REFERENCE0 A0
    #define PIN_REFERENCE1 A1
    #define PIN_REFERENCE A2

	#define DAC_CS 21
	#define DAC_SDI 20
	#define DAC_SCK 19

	#define ADC_CNVST 2
	#define ADC_SDO 1
	#define ADC_SCK 0
#elif (BOARD_REV == REV_V2)
    #define PIN_REFERENCE0 24//2
    #define PIN_REFERENCE1 25//3
    #define PIN_REFERENCE A11 //same pin as digital input 0

	#define DAC_CS 41//10
	#define DAC_SDI 40//11
	#define DAC_SCK 39//14

	#define ADC_CNVST 30 //28
	#define ADC_SDO 31 //1
	#define ADC_SCK 32 //27
#endif


#endif

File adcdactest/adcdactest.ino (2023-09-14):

/*
 *mostly stable up to 720 MHz overclock with the v1.0 board, timings may need to be adjusted
*/

#include "adc.h"
#include "dac.h"

#define LED_PIN 13
#define DI0 2
#define DI1 3
#define ANALOG_PIN A10 //TODO not actually connected

#define USE_INTERNAL_ADC false

//https://registry.platformio.org/libraries/ftrias/TeensyThreads may be helpful for simultaneous read and write
//TODO compare to inbuilt ADC (using one of the digital input pins) -- need to grab BNC splitter

void readTest();
void writeTest();
void linearityTest();

double mean(double[], unsigned int);
double stdev(double[], unsigned int);

void setup(){
	Serial.begin(115200);
	Serial.println("starting...");
	initADC();
	initDAC();

    #if USE_INTERNAL_ADC
        pinMode(ANALOG_PIN, INPUT);
        analogReadResolution(12);
        analogReadAveraging(1);
    #endif
	
}

void loop(){
	if(Serial && Serial.available()) {
		if (Serial.read() == 'g'){
			Serial.println("\nLinearity Test:");
			linearityTest();
			Serial.println("\nRead Test:");
			readTest();
			Serial.println("\nMultiple Read Test:");
			readMultipleTest();
			Serial.println("\nWrite Test:");
			writeTest();
            writeDACVolts(0.5);
		//delay(10000);
		}
		else{
			Serial.println("\nEnter 'g' to run test\n");
		}
	}
}

void readTest(){
	const uint32_t NUM_POINTS = 10000;
	uint16_t values[NUM_POINTS];
	double voltvalues[NUM_POINTS];
	writeDACVolts(1);
    #if USE_INTERNAL_ADC
        analogReadAveraging(1);
    #endif
	elapsedMicros sincestart;
	for(uint16_t i=0; i < NUM_POINTS; i++) {
        #if USE_INTERNAL_ADC
            values[i] = analogRead(ANALOG_PIN);
        #else
    		values[i] = readADC();
        #endif
	}
	float readtime = (float)sincestart/NUM_POINTS;
	for(uint16_t i=0; i < NUM_POINTS; i++) {
        #if USE_INTERNAL_ADC
	    	voltvalues[i] = 3.3*values[i]/4095;
        #else
            voltvalues[i] = ADC_BITS2VOLTS(values[i]);
        #endif
	}
	double value = mean(voltvalues, NUM_POINTS);
	double dev = stdev(voltvalues, NUM_POINTS);
	Serial.printf("Read Time: %f us \t Value: %f V \t Deviation: %f V\n", readtime, value, dev);
}

void readMultipleTest(){
	const uint8_t pointspower = 4;
	const uint16_t points = 0x1 << pointspower;
	const uint32_t NUM_POINTS = 1000;
	uint16_t values[NUM_POINTS];
	double voltvalues[NUM_POINTS];
	writeDACVolts(1);
    #if USE_INTERNAL_ADC
        analogReadAveraging(points);
    #endif
	elapsedMicros sincestart;
	for(uint16_t i=0; i < NUM_POINTS; i++) {
        #if USE_INTERNAL_ADC
            values[i] = analogRead(ANALOG_PIN);
        #else
    		values[i] = readADCMultiple(pointspower);
        #endif
	}
	float readtime = (float)sincestart/NUM_POINTS;
	for(uint16_t i=0; i < NUM_POINTS; i++) {
        #if USE_INTERNAL_ADC
	    	voltvalues[i] = 3.3*values[i]/4095;
        #else
            voltvalues[i] = ADC_BITS2VOLTS(values[i]);
        #endif
	}
	double value = mean(voltvalues, NUM_POINTS);
	double dev = stdev(voltvalues, NUM_POINTS);
	Serial.printf("Points: %i \t Read Time: %f us (%f us/pt) \t Value: %f V \t Deviation: %f V\n", points, readtime, readtime/points, value, dev);
}

void writeTest(){
	const uint32_t NUM_POINTS = 10000;
	elapsedMicros sincestart;
	for(uint16_t i=0; i < NUM_POINTS; i++) {
		writeDACVolts((float)i/NUM_POINTS);
	}
	float writetime = (float)sincestart/NUM_POINTS;
	float value = readADCVolts();
	Serial.printf("Write Time: %f us\tValue: %f V\n", writetime, value);
}

void linearityTest(){
	const uint32_t NUM_POINTS = 100;
	double values[NUM_POINTS];
	double measurements[NUM_POINTS];
	double ratio[NUM_POINTS];
	for(uint32_t i=0; i < NUM_POINTS; i++){
		values[i] = (float)(i+1)*DAC_VREF/NUM_POINTS; //don't write zero
		writeDACVolts(values[i]);
		delay(10); //let it settle
        #if USE_INTERNAL_ADC
            measurements[i] = analogRead(ANALOG_PIN)*3.3/4095;
        #else
    		measurements[i] = readADCVolts();
        #endif
		if (values[i] == 0 && measurements[i] == 0)
			ratio[i] = 1;
		else if (values[i] == 0 && measurements[i] != 0)
			ratio[i] = 0;
		else
			ratio[i] = measurements[i]/values[i];
		Serial.printf("wrote %f \t read %f \t ratio %f\n", values[i], measurements[i], ratio[i]);
	}
	Serial.printf("ratio mean: %f \t ratio stdev: %f\n", mean(ratio, NUM_POINTS), stdev(ratio, NUM_POINTS));
}


double mean(double arr[], unsigned int arr_len){
	double total = 0;
	for(uint32_t i = 0; i < arr_len; i++) {
		total = total + arr[i];
	}
	return total/arr_len;
}

double stdev(double arr[], unsigned int arr_len){
	
	double avg = mean(arr, arr_len);
	double total = 0;
	
	for(uint32_t i = 0; i < arr_len; i++) {
		total += (arr[i] - avg)*(arr[i] - avg);	
	}
	return sqrt(total/(arr_len-1));	
}

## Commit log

2020-09-25 changing to be used with teensy 3.2
2020-09-25 added code to set voltage
2020-10-06 上传文件至 ''
2020-10-14 set default to high input via pullup resistor
2022-02-17 added code for the Teensy 3.2
2022-09-28 added code that prints the input extrema and increases read averages for calibration data
2023-01-27 committing current changes to feedback controller before adding multi-state inputs
2023-09-14 added prototype control code
2023-09-15 added voltage to print output
2024-10-26 removing git subdirectories
    [82808747.xlsx, digikey cart.xlsx, feedbackController-B_Cu.gbl, feedbackController-B_Cu.gbr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]
